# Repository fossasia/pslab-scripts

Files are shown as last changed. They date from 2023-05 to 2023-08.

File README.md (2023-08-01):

# PSLab

This repo is used for scripts and operators that collect data of specific sensors connected with the PSLab.




PSLab is a tiny pocket science lab that provides an array of equipment for doing science and engineering experiments. It can function like an oscilloscope, waveform generator, frequency counter, programmable voltage and current source and also as a data logger. Our website is at https://pslab.io

## The PSLab Sensor Box

For a quick start jump to the [initial setup](#initial-setup) or the [basic usage](#basic-usage) section.

<p align="center">
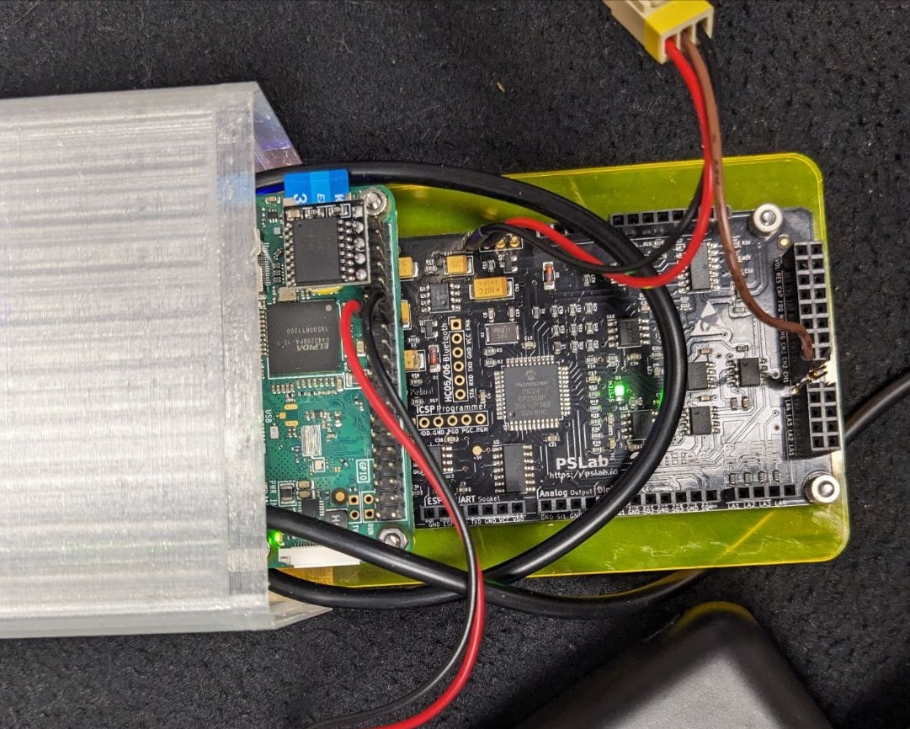
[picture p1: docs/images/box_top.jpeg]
PSLab Sensor Box
    
</p>

In this project four different experimental setups of the [PSLab v5](https://pslab.io/wp-content/uploads/PSLab-Data-Sheet.pdf) are created, each incorporating a different sensor: one measuring [CO2](/docs/sensors.md#⬛-co2e-sensor-ccs811), one for [oxygen](/docs/sensors.md#🟦-oxygen-sensor-ao-03), one for [temperature](/docs/sensors.md#🟩-temperature-sensor-lm35), as well as one setup measuring the [light intensity in lux](/docs/sensors.md#🟨-light-intensity-sensor-gl5528).
Details for those sensor setups can be found in the [docs](/docs/sensors.md).

In addition, the following **hardware components** are connected to the PSLabs:

- A **Raspberry Pi Zero W** to store the sensor data permanently on an SD card and, at the same time, make this data available via the Raspberry Pi's WiFi module. The "Zero" is especially handy here, as it is the most lightweight Raspberry Pi version. Both, the Raspi and the PSLab are screwed on to a plexiglass panel that is slid into the box using the boxe's integrated rail system.
- A **Button** to safely shutdown the Raspberry Pi. It needs to be long pressed for at least one second in order to trigger the device's shutdown. Here, one button terminal is plugged into GPIO pin 27, while the other terminal is plugged to the ground.
- The high accuracy I²C **real time clock (RTC)** model [DS3231](https://www.analog.com/media/en/technical-documentation/data-sheets/DS3231.pdf). It contains a small battery and ensures that the device's time progresses, even if the main power source is unavailable. This RTC therefore makes timestamps in the output data possible during times, where the PSLab sensor box can not access the internet. The five pins of this Pi HAT are plugged into pins 1, 3, 5, 7 and 9 of the Raspberry Pi Zero W.
- A 3D printed, splashproof [casing](/docs/casing/README.md) with a USB c port and a lasercut shield to hold the electronics securely in place.

The following **features** are implemented on top of that:

- Each measured data point is then immediately shared via OSC as `/<item_name> <measured_value>, <unit>, <timestamp>`. Additionally it is written into the CSV file of this measurement session. The file is structured as `<timestamp>, <measured_value>, <unit>, <item_name>`.
- The devices are connected to a public WiFi Network, where they share their data as part of an IoT approach. Initially, each device opened their own WiFi Hotspot, however this was later **discontinued**, as the new requirement of accessing all devices within one common network came up.
- A [samba file sharing server](https://raspberrypi-guide.github.io/filesharing/filesharing-raspberry-pi) makes the folder "/home/foss/data" of the Raspberry Pi publicly available to all devices within the WiFi Hotspot. This also enables users to modify or delete the CSV measurement data within this folder remotely via their PC or mobile phone. The measurements are not only provided to this file sharing server in real-time, but also stored on the SD card permanently.
- The measurement it triggered automatically after startup. This is done by a custom [systemd](https://www.raspberrypi-spy.co.uk/2015/10/how-to-autorun-a-python-script-on-boot-using-systemd/) service.
- The Raspberry Pi itself is running the code from the master branch this Github repository. This makes code updates easy to distribute on all devices. All PSLab sensor boxes run the exact identical code, with the only difference being the experiment type parameter with which `init_pipe.py` is called by the systemd service.

## Accessing the Raspberry Pi

In order to modify the software, the data on the Raspberry Pi's SD card needs to be accessed.
This can either be done by plugging the SD card into a computer, accessing the Raspberry Pi via SSH, or by using the Raspi as a computer itself. In the following, the latter two methods are explained in detail.
In any case, the SD card should never be cleared fully, because this would delete the operating system and therefore stop the Raspberry Pi from working.

### Using the Raspberry Pi as an Independent Computer

Here, a monitor needs to be connected to the microHDMI slot of the Raspi. Simultaneously a mouse and a keyboard need to be linked to the inner microUSB slot via an USB hub. Make sure to perform this cabling-up before attaching the device to the electricity source.

### Accessing the Raspberry Pi via SSH

An [SSH access](https://itsfoss.com/ssh-into-raspberry/) can be more convenient, as there is no additional cabling needed.
However, to establish this connection, the Raspberry Pi needs to be in the same WiFi network as the connecting laptop. If that is not the case yet, there is no way around connecting the Raspi to a monitor first, in oder to set up this WiFi connection, as the Raspberry Pi Zero W does not have a LAN port. Also, the network specific **IP address** of the Raspberry Pi needs to be known. It can be retrieved by executing the command `ifconfig` in the Raspi's terminal while having it connected to a monitor. The IP address can then usually be found in the "wlan0" paragraph and is formatted in a "000.000.000.000" pattern.
To then establish the ssh connection, the following steps need to be executed:

1. Ensure that the PC is connected to the same WiFi Hotspot as the PSLab Sensor Box.
2. Open the SSH connection by running `ssh foss@<ip>` in the PC's terminal and entering the password `foss` when asked.
3. Now you are operating on the Raspberry Pi.

## Initial Setup

Before using the devices in an own network, a one time setup is needed.
Once this is done, for every following usage, please directly jump to the [basic usage](#basic-usage) section.

Both, the OSC messages and the CSV file, of the measurement can be retrieved via WiFi.
Currently, the devices are connected to a dummy WiFi Hotspot with the credentials `myHotspot` as the SSID and `password123` as the password.
Thus, for basic testing, one can just open a Hotspot with these details on a Phone/PC, the devices will automatically connect and the measurement data can be obtained.

However, for more extensive usage, it is obviously more convenient to connect the PSLab Sensor Boxes to the buildings usual WiFi.
For example a connection to eduroam can be established by [logging in with one's university credentials](https://www.uni-weimar.de/fileadmin/user/uni/zentrale_einrichtungen/scc/wlan/Ubuntu.pdf).
The network connection can be changed by [connecting the Raspberry Pi to a monitor](#using-the-raspberry-pi-as-an-independent-computer) and logging into the new WiFi Hotspot using the graphical user interface. Once connected, it is also possible to [set a static private IP address](https://www.tomshardware.com/how-to/static-ip-raspberry-pi) for the Raspberry Pi in this network.
This can be very useful, for example, in order to make the Raspi reliably accessible via SSH.
Please make sure that the devices can see each other in the network and disable/ reconfigure the [VLAN](https://www.techtarget.com/searchnetworking/definition/virtual-LAN), in case one is set up.

Additionally, the IP address and port of the OSC server, need to be edited according to the actual address of the OSC receiver.
This can be done by adjusting the `OSC_RECEIVER_IP` and the `OSC_RECEIVER_PORT` constants on the Raspberry Pis.
The only loophole to this, is to use a OSC server at the pre-configured IP address of `192.168.173.152`.
However, that's not always possible, depending on the available namespace of the network.

## Basic Usage

Once a power source (power bank or cord to electricity outlet) is connected to the PSLab sensor box and the device has fully booted (this **may take a minute ot two**), a new measurement is automatically started. The measurement results are now simultaneously shared via the [Open Sound Control Protocol (OSC)](https://en.wikipedia.org/wiki/Open_Sound_Control) and collected in a [CSV](https://en.wikipedia.org/wiki/Comma-separated_values) file.
To retrieve this data, please connect your own PC/Phone to the same public WiFi Hotspot, that the PSLab Sensor Box is connected to (see [initial setup](#initial-setup)).

### Accessing the CSV Measurements

The CSV measurements of each PSLab sensor box can be retrieved in real time from the file server via WiFi:

1. A detailed manual on how to connect to the devices file server for the first time can be found in the [docs](/docs/network_connection_manual.md).
2. Once connected, the PSLab will appear in the "Network Devices" section.
<p align="center">
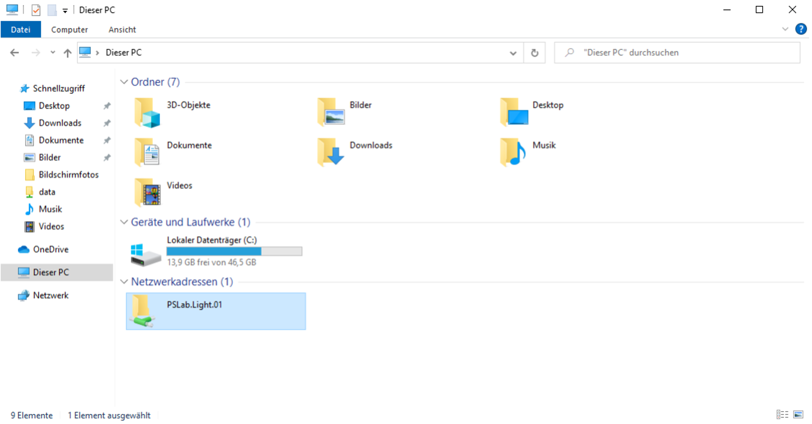
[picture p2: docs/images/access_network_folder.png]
Access network device
    
</p>
Access the data folder and fetch the most recent CSV measurement data file. This file can for example be opened by Excel or just a normal text editor. The current measurement file is updated automatically every few seconds, to see these real time changes, just close and reopen the file.

<p align="center">
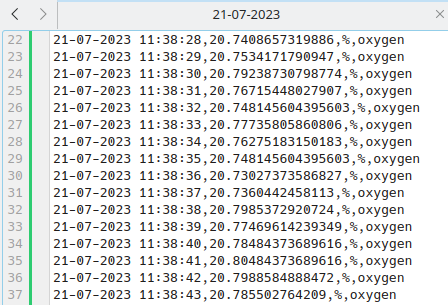
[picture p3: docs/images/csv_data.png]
Sample CSV
    
</p>

Analysis tasks can now be performed on these data sheets, for example by importing them into [Jupyter Notebook](https://jupyter.org/).

### Receiving the OSC Messages

The OSC messages are sent to the specified IP address upon startup. To receive those messages a OSC server like this is necessary:

```[python]
import argparse
from pythonosc.dispatcher import Dispatcher
from pythonosc import osc_server

if __name__ == "__main__":
    parser = argparse.ArgumentParser()
    parser.add_argument("--ip", default="192.168.173.152")
    parser.add_argument("--port", type=int, default=5005)
    args = parser.parse_args()

    dispatcher = Dispatcher()
    dispatcher.map("/light", print)
    dispatcher.map("/temp", print)
    dispatcher.map("/co2", print)
    dispatcher.map("/oxygen", print)

    server = osc_server.ThreadingOSCUDPServer(
        (args.ip, args.port), dispatcher)
    server.serve_forever()
```

This server uses the [python-osc](https://github.com/attwad/python-osc) package to receive and decode the messages. The package can be installed by executing `pip3 install python-osc` in the PC's terminal.
Please note that this setup only works if the IP address, specified as `OSC_RECEIVER_IP`, is identical to the IP address stated in the server scrips (in line 7 here) and corresponds to the laptops own IP address (obtainable by executing "ifconfig" in the terminal). This OSC server for example produces the following output when, at the same time, the Oxygen Sensor Box and the Light Sensor Box are sending OSC data to this IP address at port 5005:

<p align="center">
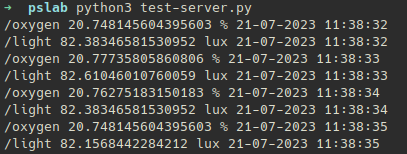
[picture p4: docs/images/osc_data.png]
Sample OSC
    
</p>

### Example Measurement Session

When for example using the PSLab Sensor Box "Lux", changes in the environment's light intensity can be measured.
After attaching the box to a power bank and waiting for two minutes, the device starts measuring.

<p align="center">
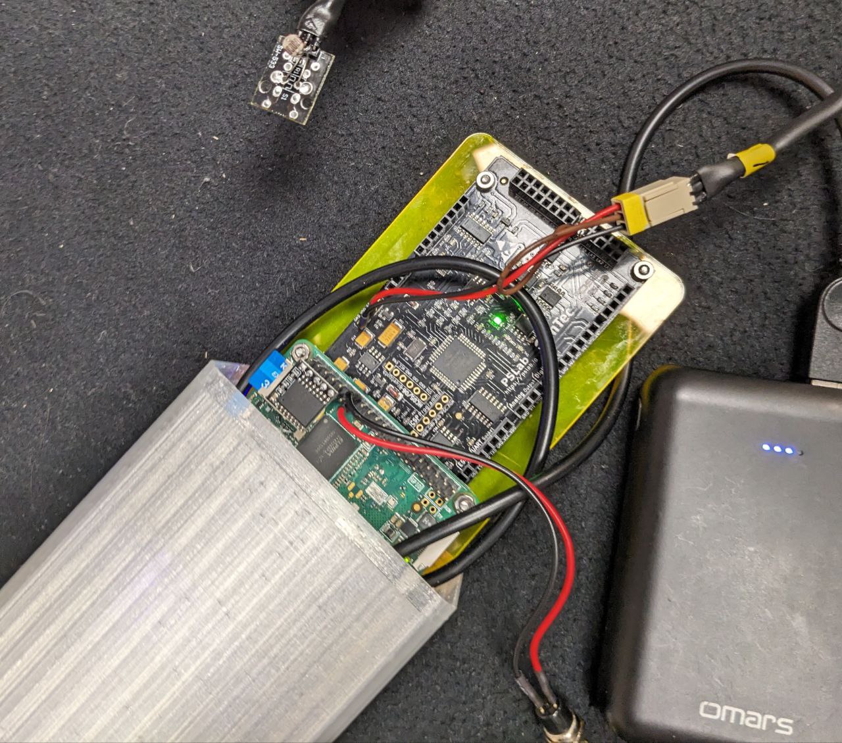
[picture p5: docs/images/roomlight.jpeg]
Lux sensor at room light
    
</p>

The running OSC server on our laptop, that is connected to the same WiFi Hotspot as the Sensor Box, then receives the following data:

```
/light 109.5234702837157 lux 21-07-2023 20:44:12
/light 108.62976013160224 lux 21-07-2023 20:44:13
/light 114.54458695414951 lux 21-07-2023 20:44:14
```

To test the sensor and observe the changes in the environment, the lights are now turned off.

<p align="center">
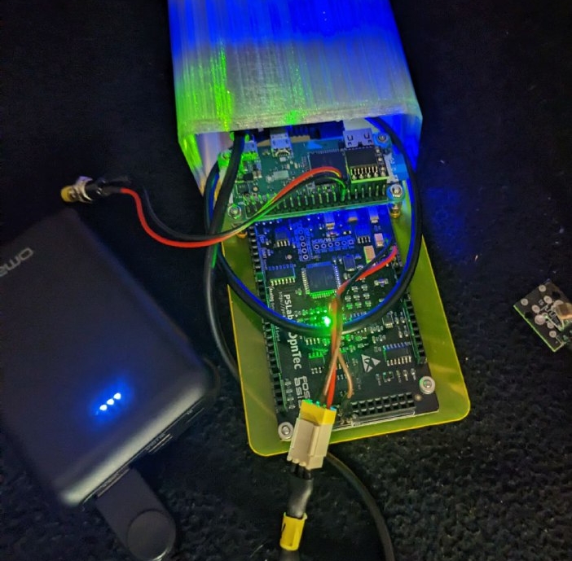
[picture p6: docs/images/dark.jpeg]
Lux sensor at darkness
    
</p>

This results in the following OSC messages:

```
/light 6.80740388396548 lux 21-07-2023 20:46:04
/light 7.05431189748499 lux 21-07-2023 20:46:05
/light 7.52577384043171 lux 21-07-2023 20:46:06
```

To then test the sensor at a very hight brightness, we turned the lights on again and exposed the photoresistor to a flashlight:

<p align="center">
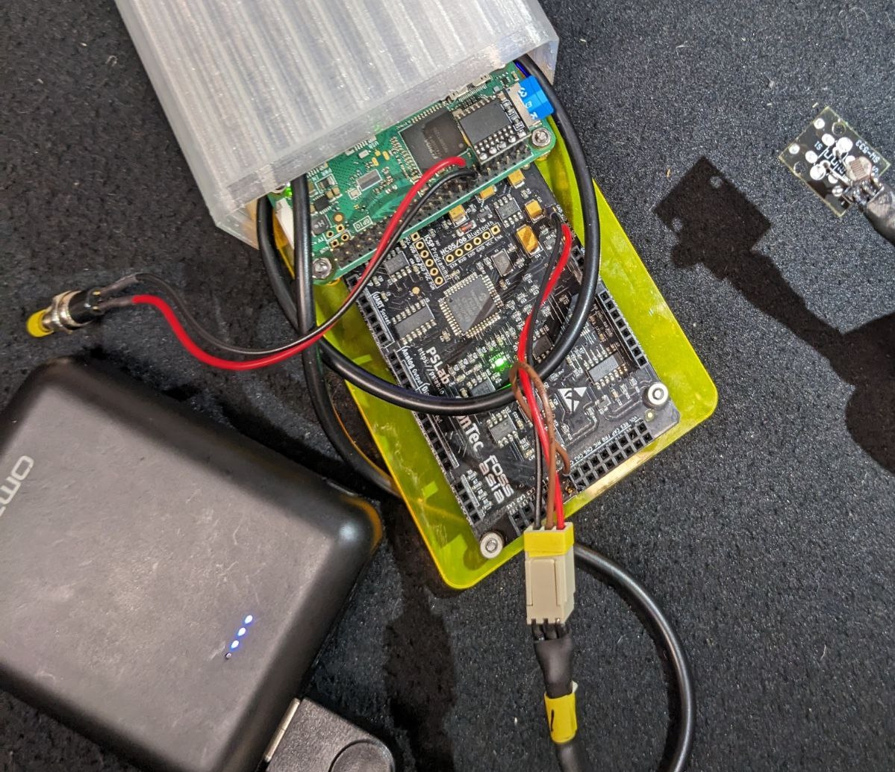
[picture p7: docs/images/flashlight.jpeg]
Lux sensor at flashlight
    
</p>

Thus, the OSC server receives these messages:

```
/light 1721.79974583536023 lux 21-07-2023 20:47:38
/light 1902.29013779831879 lux 21-07-2023 20:47:39
/light 1483.70672770591856 lux 21-07-2023 20:46:40
```

In an analogue way, the temperature sensor can be tested by warming it up with one's finger tips,
while the CO2 and oxygen sensors can by tested by exposing them to exhaled air.

### Ending the Session

To eventually trigger the shut down process of the Raspberry Pi, please press the attached button for one to two seconds.
After waiting 20-30 seconds, the shut down is completed, the green indication light on the Raspberry Pi goes off and the electricity source can be unplugged.
Technically, the measurement session can also be terminated by just unplugging the power source directly, however in the long term,
this technique can be harmful for the Raspberry Pi's file system.

## Debugging

As this is a hardware project, it is not unlikely that at some point in time, one of the cables or other components will cause problems. To then solve this, it is important to localize the error. Here, different levels of debugging can help, depending on the supposed location of the problem.
Basic debugging steps may be:

- Turn the Raspberry Pi off (by using the button) and on again (by plugging in a power bank).
- Make sure all cables are attached firmly. Try unplugging and reattaching them.
- Sometimes the output voltage of a laptop's USB port might vary a bit to much, try using a power bank instead.
- Make sure the lights on the PSLab are glowing. Otherwise there probably is a problem with the boxes' charging cable or the PSLab itself.
- Make sure the light on the Raspberry Pi is glowing or blinking. This indicates a successful booting of the Raspbian OS.
- Try using one PSLab Sensor Box after another, not in parallel.
- If the device does not connect to the WiFi network (for example checkable via Linux' `nmap` tool), try having the network open already during the Raspberry Pi's booting process.
- Try opening the Hotspot, that the Sensor Boxes are connected to, from another device (e.g. phone, instead of laptop).

Some more advanced debugging techniques include the following:

### Debugging Sensor Issues - On a PC

To ensure that the PSLab itself and the sensor are working properly,  the following test can be executed.
Please note that this routine is the only one that is executed on a normal (Linux)
**PC, instead of the Raspberry Pi**, in order to abstract from any Raspi specific problems.

1. Ensure that python3 is installed on your PC by running `python3 --version` in the terminal. In case there is no item found, install version 3.6 by `sudo apt-get install python3.6` and reboot your system afterwards to ensure that everything is fully loaded.
2. Install the pslab-python library on the PC by executing `pip3 install pslab`.
3. Detach the PSLab and the corresponding sensor from the Raspberry Pi by removing the
microUSB to microUSB cable between Raspi and PSLab. Instead connect the microUSB port of the PSLab to one of the PC's USB ports.
4. Download the pslab-scripts library by running `sudo git clone https://github.com/fossasia/pslab-scripts.git`.
5. Open the repository folder by executing `cd pslab-scrips`.
6. Start the execution a sensor type specific test by running `sudo python3 init_pipe.py <type>` (for example
`sudo python3 init_pipe.py oxygen`). This execution can always be stopped by hitting ctrl+c.
7. Check the fetched measurement data by accessing the file located in `/home/<user name>/data`.

### Debugging the Startup Script - On the Raspberry Pi

Often times the script itself actually works fine, but the startup manager might start it
too early, causing resource conflicts and other issues to arise.
One option to debug this, is to first make sure that the script itself works fine by running `sudo python3 /home/foss/code/init_pipe.py <type>`
on the Raspberry Pi (for example `sudo python3 init_pipe.py oxygen`) and checking the results in
`/home/foss/data`. If those results look good, but the data fetching upon startup still does not work, the error logs of the startup script can be examined by executing `journalctl -u startup.service --since yesterday` in the Raspi's terminal.

## Advanced Usage

Different software and hardware projects can be realized on this combination of PSLab and Raspberry Pi.
Some ideas for modifying the existing software are listed below.
As python3, the pslab-python library, as well as this pslab-scripts repository, are already installed on the Raspberry Pis, **no** additional installation is needed here.

### Adjusting the measurement interval

Currently a new data point is retrieved from the sensor every second. This can be changed by adjusting the value for the`MEASURING_INTERVAL`. This constant can be found in the `/home/foss/pslab-scripts/measure.py` file on the Raspberry Pi.

### Adjusting the flushing interval

The data points are flushed into the CSV file after every 10 measurements in the current implementation. To change this, the `FLUSHING_THRESHOLD` value in `/home/foss/pslab-scripts/store_data.py` can be adjusted on the Raspi.

### Accessing the continuous measurement data stream via an API

As of now, the measurement data is redirected into a CSV file and OSC messages by the pipe function. This can however be modified freely, for example by adding an additional step 
to transform and output some data into the data exporting function.
This new process can freely process the measured data points, received via `connection.recv()`.

### Fetching a software update from Github

1. Open the terminal.
2. Open the folder "pslab-scripts" by typing `cd /home/foss/pslab-scripts`.
3. Enter `git pull` in the terminal to fetch the new changes in software.

### Changing the sensor type

By adjusting the experiment type parameter in the systemd service "startup.service", the supported sensor type of this specific PSLab sensor box can be changed easily:

1. Open a terminal.
2. Type `sudo nano /lib/systemd/system/startup.service`.
3. The "startup.service" file is now opened in a simple text editor. Here, you can adjust the experiment type parameter, e.g. from "light" to "co2", in case the PSLab sensor box for light shall now be used with a CO2 sensor. Besides "light" and "co2", also "oxygen" and "temp", are supported as parameters here.
4. Save the changes by pressing ctrl+o. Exit the editor by pressing ctrl+x.
5. The changes take effect once the device is rebooted. This can for example be done by executing `sudo reboot`.

## Repository Structure

```
📦pslab-scripts
 ┣ 📂docs                               # Supplementary material
 ┃ ┣ 📂ao-03_amplifier_circuit_design  # KiCad project files of the custom circuit board for the AO-03 sensor
 ┃ ┃ ┗ 📜...
 ┃ ┣ 📂casing                          # Information about the 3d printed casing, as well as the lasercut shield
 ┃ ┃ ┣ 📜README.md
 ┃ ┃ ┗ 📜...
 ┃ ┣ 📂images
 ┃ ┃ ┗ 📜...
 ┃ ┣ 📂logos                           # Sticker designs for the boxes (made with Inkscape)
 ┃ ┃ ┗ 📜...
 ┃ ┣ 📜network_connection_manual.md    # Manual on how to connect a device to the PSLab's file server
 ┃ ┣ 📜presentation_may28.pdf
 ┃ ┣ 📜sensors.md                      # Detailed descriptions of all four sensor setups
 ┃ ┗ 📜testing_manual.md               # Detailed manual on how to test the devices
 ┣ 📂sensors                            # Contains a specific run script for every sensor
 ┃ ┣ 📜ao03_oxygen.py
 ┃ ┣ 📜ccs811_co2.py
 ┃ ┣ 📜driver_ccs811.py                # Custom driver for the CCS811 sensor
 ┃ ┣ 📜gl5528_light.py
 ┃ ┗ 📜lm35_temp.py
 ┣ 📜export_data.py                     # Sharing the measurements via OSC and CSV
 ┣ 📜init_pipe.py                       # Main project file
 ┣ 📜measure.py
 ┗ 📜shutdown.py                        # Script for the button logic
```

## Buy

* You can get a Pocket Science Lab device from the [FOSSASIA Shop](https://fossasia.com).
* More resellers are listed on the [PSLab website](https://pslab.io/shop/).

## Communication

* The PSLab [chat channel is on Gitter](https://gitter.im/fossasia/pslab).
* Please also join us on the [PSLab Mailing List](https://groups.google.com/forum/#!forum/pslab-fossasia).

## Site

The website is hosted on [pslab.io](http://pslab.io).

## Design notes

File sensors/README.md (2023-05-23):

Currently the following sensors are supported by specific firmware here, however [others](https://pslab.io/sensors/) could be added later on.

## CO<sub>2</sub>e Sensor: [CCS811](https://cdn.sparkfun.com/assets/learn_tutorials/1/4/3/CCS811_Datasheet-DS000459.pdf)

This digital sensor is embedded on the [CJMCU-8118](https://www.amazon.co.jp/-/en/CJMCU-8118-HDC1080-Monoxide-Temperature-Humidity/dp/B07KWPHYLY) circuit board and powered by a custom [driver](https://github.com/fossasia/pslab-python/tree/development/pslab/external) that uses the sensors I²C protocol.

The CCS811 measures the [CO<sub>2</sub>e](https://klima.com/blog/what-is-co2e/) ("CO<sub>2</sub> equivalent") value of the surrounding air in particles per million (ppm). This value also incorporates the levels of methane (CH<sub>4</sub>), nitrous dioxide (N<sub>2</sub>O) and other synthetic gases, besides the regular CO<sub>2</sub> measurement, which makes up about 75% of the CO<sub>2</sub>e. This value is therefore used by environmental scientists nowadays to give more accurate measurements about the current levels of emissions in the air.

As emissions vary depending on the air's temperature and humidity, the CCS811 sensor has inbuilt temperature and moisture sensors. It uses those to offset the variation of the measuring conditions to the optimal lab conditions. However, it is important to notice that the sensor has a lower limit of 400ppm CO<sub>2</sub>e that can be detected.

## Oxygen Sensor: [AO-03](http://www.aosong.com/userfiles/files/media/Datasheet%20AO-03.pdf)

The analog AO-03 sensor measures the O<sub>2</sub> content of the surrounding air in percent (%). It is embedded in a custom circuit board that is amplifying the measured voltage, because the changes in oxygen levels are usually just very slight and therefore the changes in voltage are also only minimal.

<p align="center">
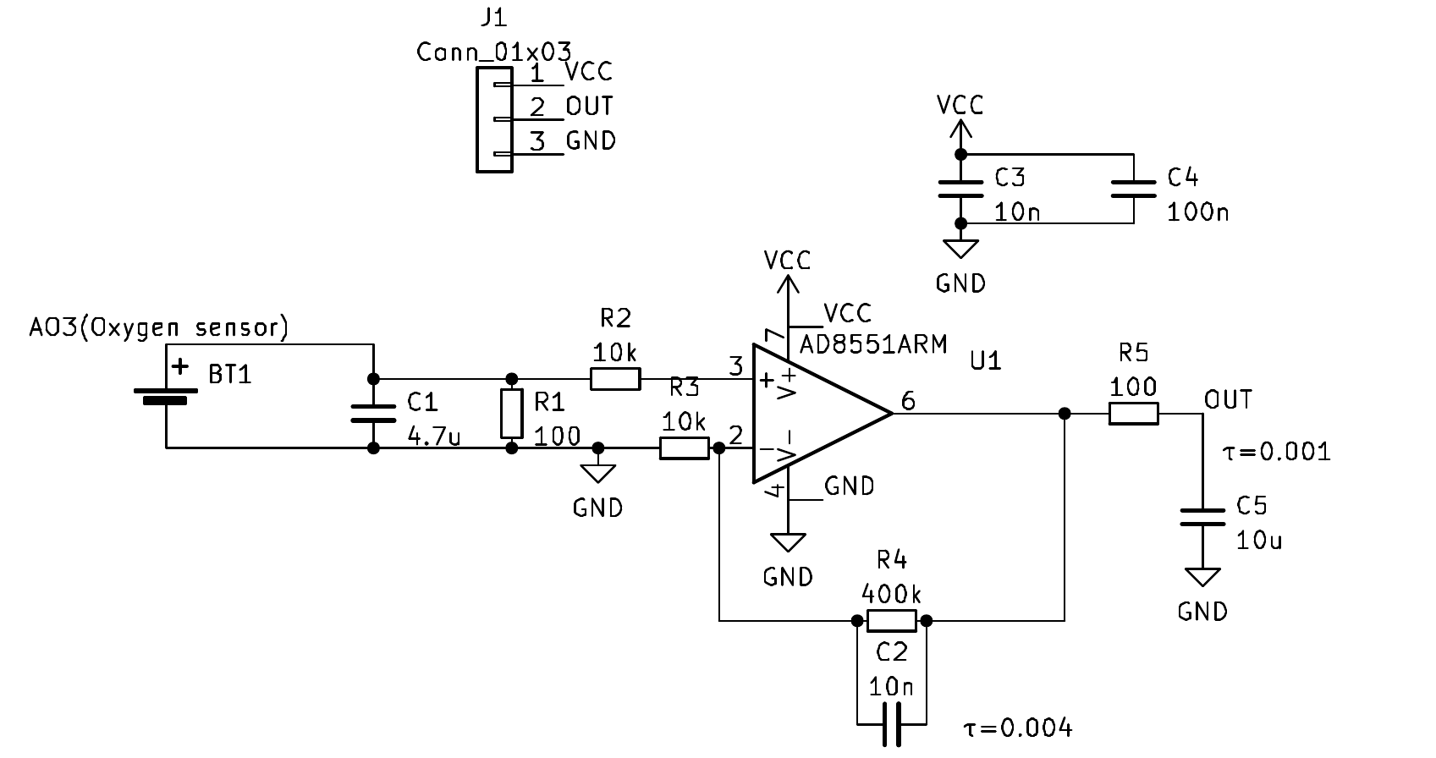
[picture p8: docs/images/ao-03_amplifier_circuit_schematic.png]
Schematic of the amplifier board
    
    <p>[Custom designed](../docs/ao-03_amplifier_circuit_design/) amplifying circuit board for the AO-03 oxygen sensor.</p>
</p>

## Light Intensity Sensor: [GL5528](https://pi.gate.ac.uk/pages/airpi-files/PD0001.pdf)

A light sensitive photo-resistor is used to measure the luminous intensity of the surrounding light waves in lumen per square meter (lux). The resistance of this sensor is measured within a voltage divider circuit with a second resistor of 10k Ohm. This value can then easily be transformed into the actual light intensity. Be aware that the luminous intensity is rising exponentially fast with increasing brightness levels of the environment.

## Temperature Sensor: [LM35](https://www.ti.com/lit/ds/symlink/lm35.pdf)

This analog thermometer can measure temperatures between −55°C and 150°C. It guarantees an accuracy of +/- 1°C over the whole range.

## Connecting the Sensors
<p align="center">
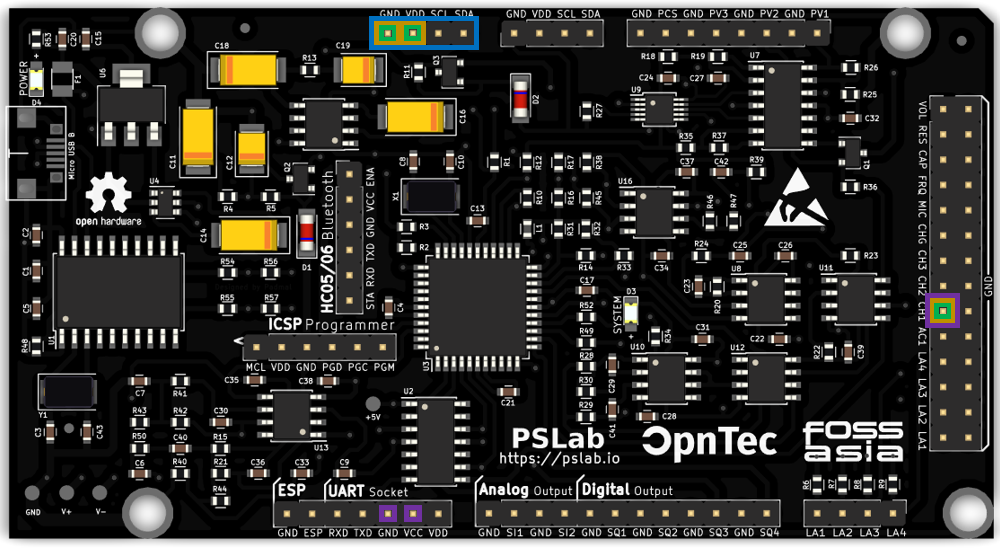
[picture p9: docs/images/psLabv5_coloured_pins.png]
Color coded sensor connections
    
</p>

- **CO<sub>2</sub>e: blue pins.** 'VCC' to the PSLab's VDD (3.3V power supply), 'GND' to the PSLab's GND, 'SLC' to the PSLab's SLC (serial clock needed for the I²C protocol) and 'SDA' to the PSLab's SDA (serial data needed for the I²C protocol).
- **Oxygen: orange pins.** 'GND' to the PSLab's GND, 'OUT' to the PSLab's CH1 (analog input to read voltages in range [-16 V, +16 V]) and 'VCC' to the PSLab's VDD (3.3V power supply).
- **Light Intensity: green pins.** '-' to the PSLab's GND, the middle pin to the PSLab's VDD (3.3V power supply) and 'S' to the PSLab's CH1 (analog input to read voltages in range [-16 V, +16 V]).
- **Temperature: purple pins.** Facing the flat side and having the sensor's pins face down: Left pin to the PSLab's VCC (5V power supply), middle pin to the PSLab's CH1 (analog input to read voltages in range [-16 V, +16 V]) and right pin to the PSLab's GND.

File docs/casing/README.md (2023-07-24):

# Casing

As part of open source approach, we want to provide a casing for the PSLab Sensor
Boxes that is individually re-creatable and editable at home.
We therefore decided to design 3d printed boxes with a removable side lid.
To securely keep the PSLab and the Raspberry Pi in place, we furthermore designed a
lasercut acrylic shield to attach the technology onto.
This shield can then be slid tightly into the rail system of the box.
As acrylic often slightly varies in thickness there are two slightly different box options with
differing rail sizes: please measure your acrylic first and then print the suitable box for it.

To make the box splashproof, a special sealing was screwed in place for the output point of the sensor cable.
Also, a USB to USB c in socket was installed to simplify attaching the device to a power source.

<p align="center">
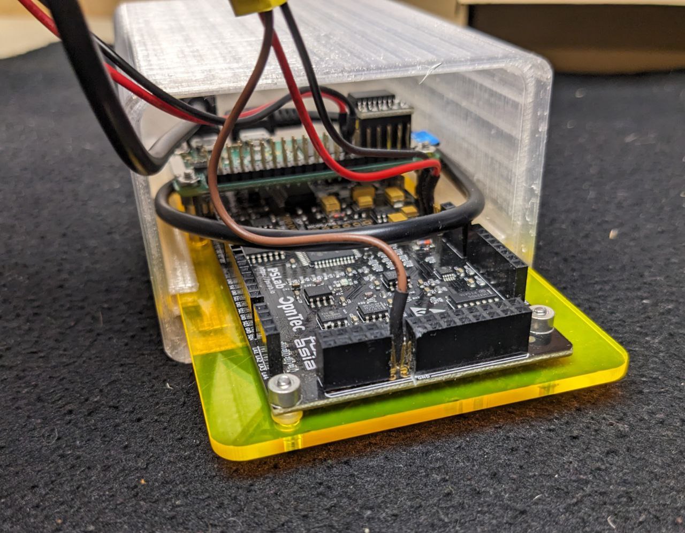
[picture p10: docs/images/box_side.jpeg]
Casing
    
</p>

## Required Materials

- An 8x14cm piece of 3mm thick acrylic
- About 100g of (PLA) filament for the boxes' body
- About 25g of (PLA) filament for the boxes' lid
- 4 x M2.5 x 10mm screws to attach the PSLab to the shield
- 4 x M2.5 washers to space the PSLab from the shield
- 4 x M2.5 x 20mm Screws to attach the Raspberry Pi to the shield
- 8 x M2.5 x 5mm or 4 x M2.5 x 10mm spacers to position the Raspberry Pi above the PSLab
- 4 x M2.5 nuts to secure the Raspberry Pi
- Optional: USB to USC c in socket, screwable sealing to output the sensor cable

## Folder Structure

```
📂casing
┣ 📂box_rail_3.5mm               # CAD model of the box made for acrylic shields of a thickness between 3.0 and 3.4 mm.
┃ ┣ 📜prusa_printing_code.gcode # This file can directly be printed on a Prusa i3 MK3S with 0.4 nozzle. Made with Prusa Slicer.
┃ ┗ 📜...
┣ 📂box_rail_3mm                 # CAD model of the box made for acrylic shields of a thickness between 2.5 and 2.9 mm.
┃ ┣ 📜prusa_printing_code.gcode # This file can directly be printed on a Prusa i3 MK3S with 0.6 nozzle. Made with Prusa Slicer.
┃ ┗ 📜...
┣ 📂lid                          # CAD model of the boxes' lid.
┃ ┣ 📜prusa_printing_code.gcode # This file can immediately be printed on a Prusa i3 MK3S with 0.4 nozzle. Made with Prusa Slicer.
┃ ┗ 📜...
┣ 📂shield                       # Lasercut model for the acrylic shield. Designed with Inkscape. Compiled with VisiCad for the lasercutter at FabLab, Berlin.
┗  ━ 📜...
```

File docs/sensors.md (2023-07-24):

# Sensor Setups

Currently the following sensors are supported by specific firmware here, however [others](https://pslab.io/sensors/) could be added later on.

## ⬛ CO<sub>2</sub>e Sensor: [CCS811](https://cdn.sparkfun.com/assets/learn_tutorials/1/4/3/CCS811_Datasheet-DS000459.pdf)

This digital sensor is embedded on the [CJMCU-8118](https://www.amazon.co.jp/-/en/CJMCU-8118-HDC1080-Monoxide-Temperature-Humidity/dp/B07KWPHYLY) circuit board and powered by a custom driver that uses the sensors I²C protocol.

The CCS811 measures the [CO<sub>2</sub>e](https://klima.com/blog/what-is-co2e/) ("CO<sub>2</sub> equivalent") value of the surrounding air in particles per million (ppm). This value also incorporates the levels of methane (CH<sub>4</sub>), nitrous dioxide (N<sub>2</sub>O) and other synthetic gases, besides the regular CO<sub>2</sub> measurement, which makes up about 75% of the CO<sub>2</sub>e. This value is therefore used by environmental scientists nowadays to give more accurate measurements about the current levels of emissions in the air.

As emissions vary depending on the air's temperature and humidity, the CCS811 sensor has inbuilt temperature and moisture sensors. It uses those to offset the variation of the measuring conditions to the optimal lab conditions. Please give the sensor a minute after startup to fully calibrate. However, it is important to notice that the sensor has a lower limit of 400ppm CO<sub>2</sub>e that can be detected.

<p align="center">
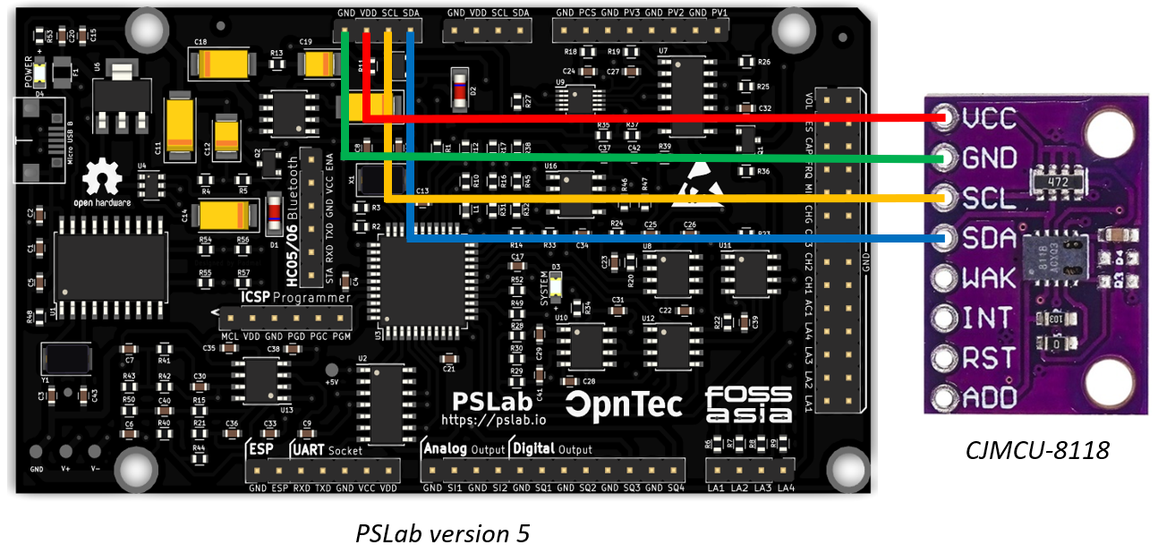
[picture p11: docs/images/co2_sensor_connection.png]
Connecting the co2 sensor
    
</p>
The CJMCU-8118 is connected to the PSLab's VDD (3.3V power supply), GND (ground), SLC (serial clock needed for the I²C protocol) and SDA (serial data needed for the I²C protocol).

## 🟦 Oxygen Sensor: [AO-03](http://www.aosong.com/userfiles/files/media/Datasheet%20AO-03.pdf)

The analog AO-03 sensor measures the O<sub>2</sub> content of the surrounding air in percent (%). It is embedded in a custom circuit board that is amplifying the measured voltage, because the changes in oxygen levels are usually just very slight and therefore the changes in voltage are also only minimal. Please give the sensor a minute after startup to fully calibrate. This AO-03 circuit board is designed as described [below](./ao-03_amplifier_circuit_design/) and depicted in the following:
<p align="center">
    Schematic of the amplifier board
</p>

<p align="center">
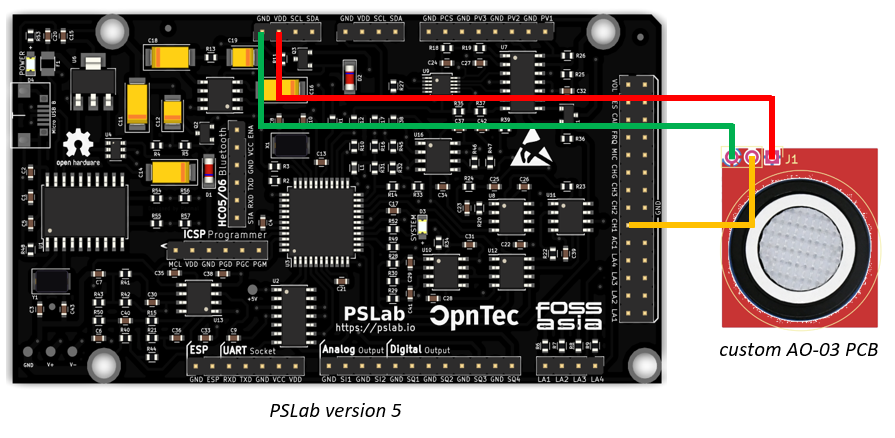
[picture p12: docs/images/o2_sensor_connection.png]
Connecting the o2 sensor
    
</p>
The circuit board is connected to the PSLab's GND (ground), CH1 (analog input to read voltages in range [-16 V, +16 V]) and VDD (3.3V power supply).

## 🟨 Light Intensity Sensor: [GL5528](https://pi.gate.ac.uk/pages/airpi-files/PD0001.pdf)

A light sensitive photo-resistor is used to measure the luminous intensity of the surrounding light waves in lumen per square meter (lux). The resistance of this sensor is measured within a voltage divider circuit with a second resistor of 10k Ohm, inbuilt in the [KY-018 circuit board](https://datasheetspdf.com/pdf-file/1402029/Joy-IT/KY-018/1). This value can then easily be transformed into the actual light intensity. Be aware that the luminous intensity is rising exponentially fast with increasing brightness levels of the environment.

<p align="center">
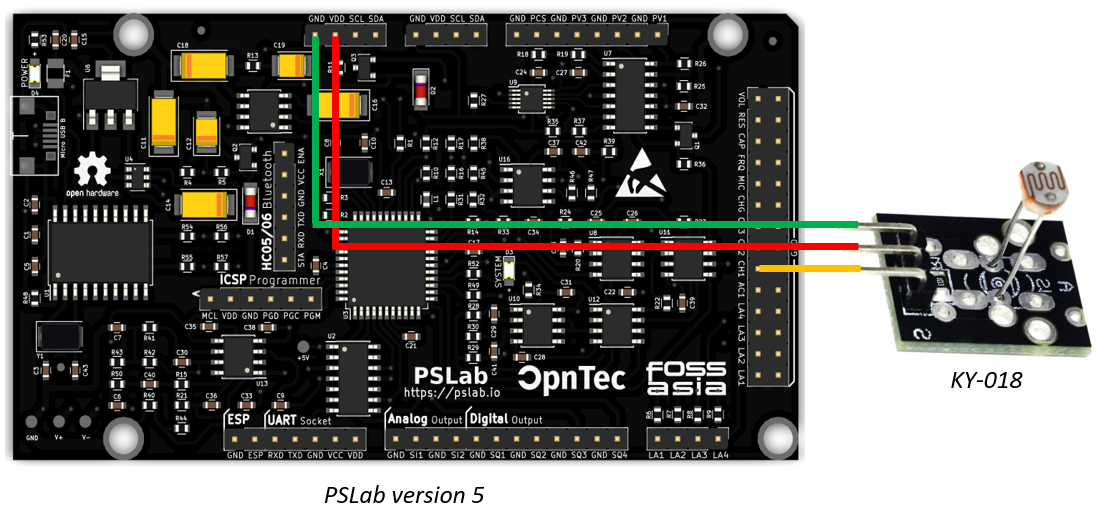
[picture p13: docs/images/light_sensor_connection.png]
Connecting the light sensor
    
</p>
The KY-018 board is connected to the PSLab's GND (ground), VDD (3.3V power supply) and CH1 (analog input to read voltages in range [-16 V, +16 V]).

## 🟩 Temperature Sensor: [LM35](https://www.ti.com/lit/ds/symlink/lm35.pdf)

This analog thermometer can measure temperatures between −55°C and 150°C. It guarantees an accuracy of +/- 1°C over the whole range.

<p align="center">
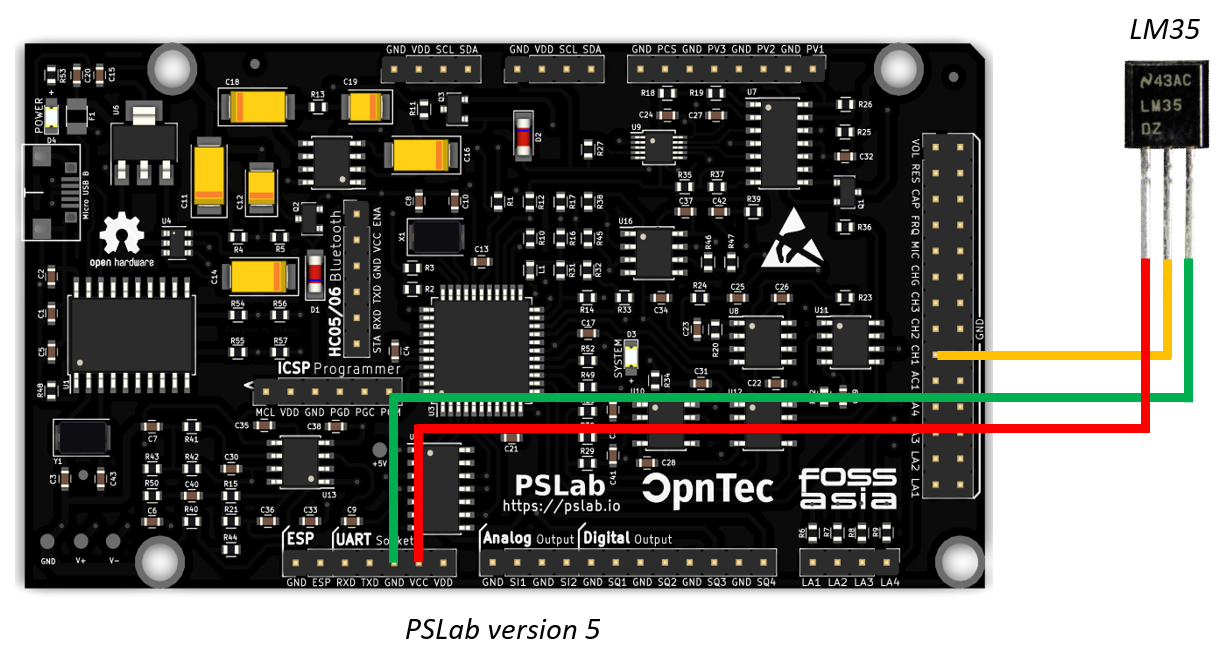
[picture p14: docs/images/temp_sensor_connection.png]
Connecting the temperature sensor
    
</p>
The LM35 is connected to the PSLab's VCC (5V power supply), CH1 (analog input to read voltages in range [-16 V, +16 V]) and GND (ground).

## Sensor Connections

The sensors are linked to the PSLab with reverse polarity protected connectors,
to enable the user to exchange sensors, without the need of unsoldering the jumper cables directly from the PSLab.
In particular, [qwiic connectors](https://www.sparkfun.com/qwiic) were used for the I²C sensors,
as well as regular 3 pin connectors for the analogue sensors.

The connecting cables are color coded as follows:

|                     | Voltage | Ground | Signal |  SDA | SCL    |
|---------------------|---------|--------|--------|----- |--------|
|      **qwiic**      |   red   |  black |        | blue | yellow |
| **3 pin to sensor** |   red   |  brown | yellow |      |        |
|  **3 pin to board** |   red   |  black |  brown |      |        |

Those connectors are then attached to the sensors by about 50cm long cables,
making it for example possible to use the sensor in a climate chamber, while
keeping the box itself outside of it.

In order to make the sensors as water and temperature resistant as possible, their PCBs are covered with conformal coating
and all pin connections are enclosed in, mostly glue coated, shrink tubing.

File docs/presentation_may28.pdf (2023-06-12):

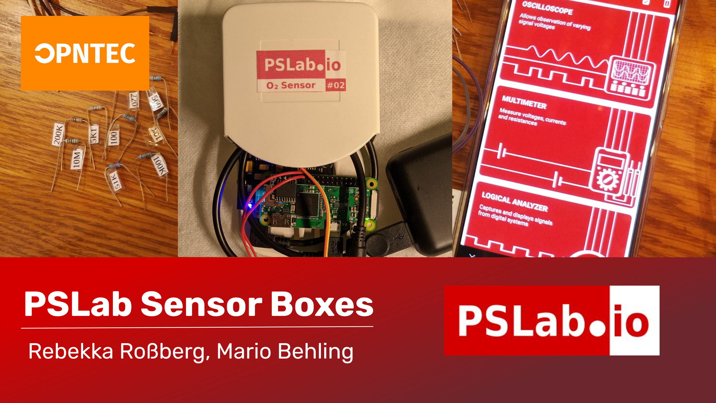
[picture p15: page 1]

# PSLab Sensor Boxes

Rebekka Roßberg, Mario Behling

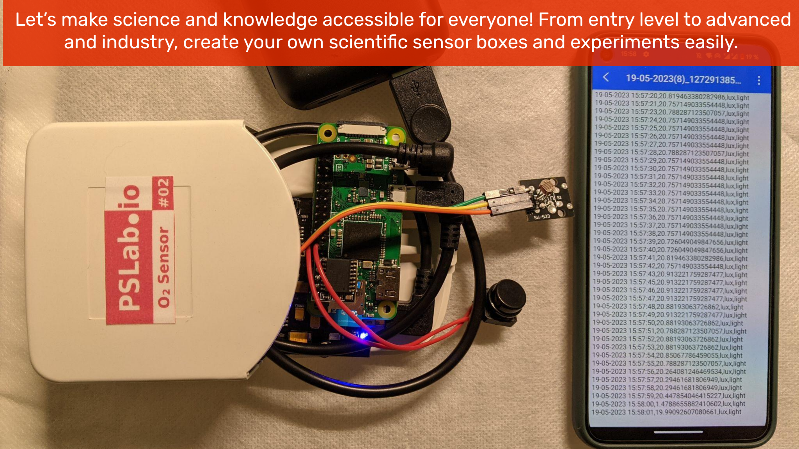
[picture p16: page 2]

Let’s make science and knowledge accessible for everyone! From entry level to advanced and industry, create your own scientific sensor boxes and experiments easily.

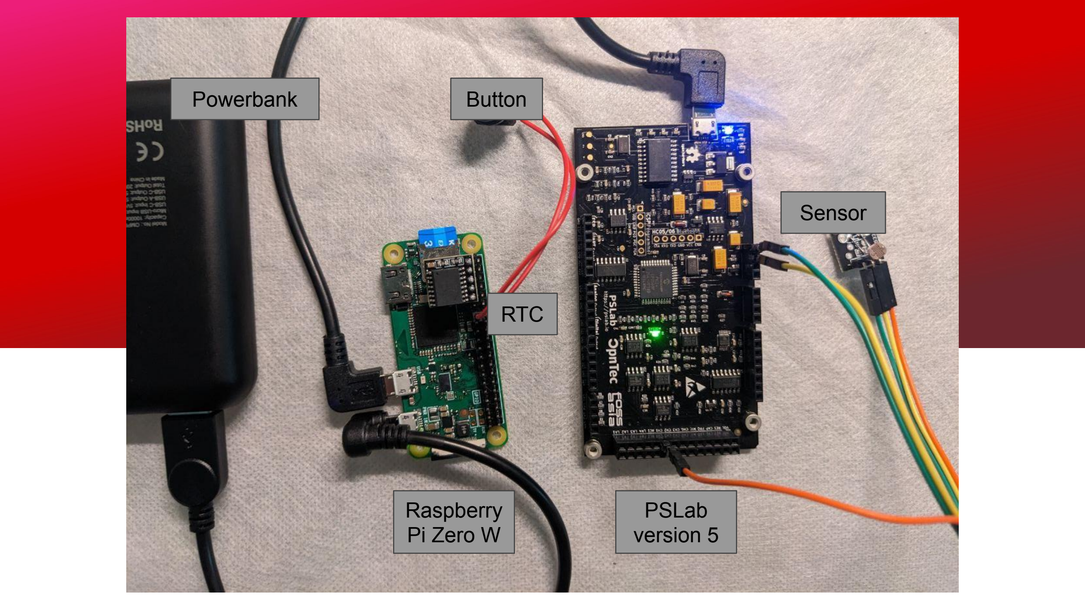
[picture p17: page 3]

Sensor

PSLab
version 5

Button

Raspberry
Pi Zero W

Powerbank

RTC

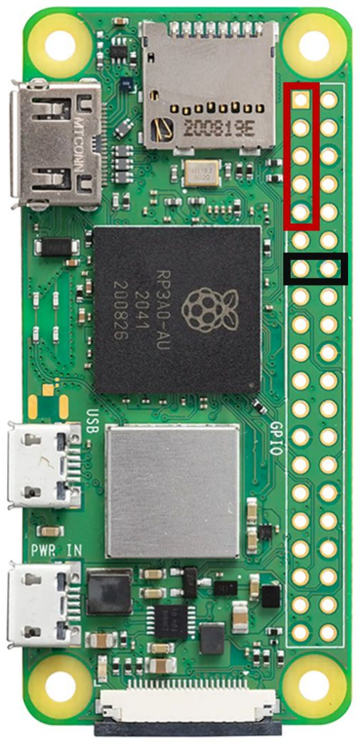
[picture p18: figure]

## Additional Hardware

❖ Raspberry Pi Zero W: for permanent data storage on the SD card and hosting of a file server via the integrated Wi-Fi Hotspot
❖ High Accuracy Real Time Clock: for network independent time stamps in the measurement data ❖ Button: for a safe shutdown
❖ Powerbank: for mobile use

## . Measuring Light Intensity

❖ Measurement in Lux
❖ Using the GL5528 photo-resistor
❖ Embedded within the KY-018’s voltage divider circuit ❖ Value on exponential scale

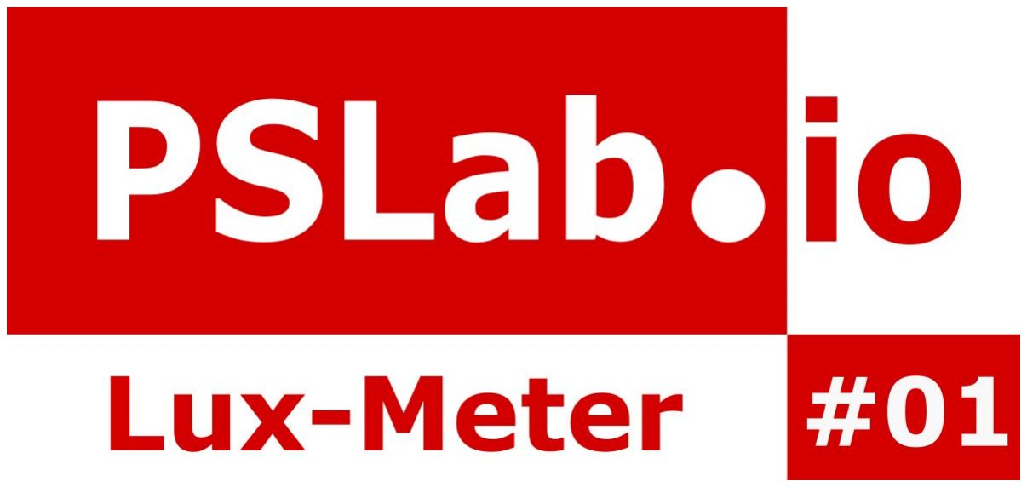
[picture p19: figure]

## Light Intensity Sensor: GL8

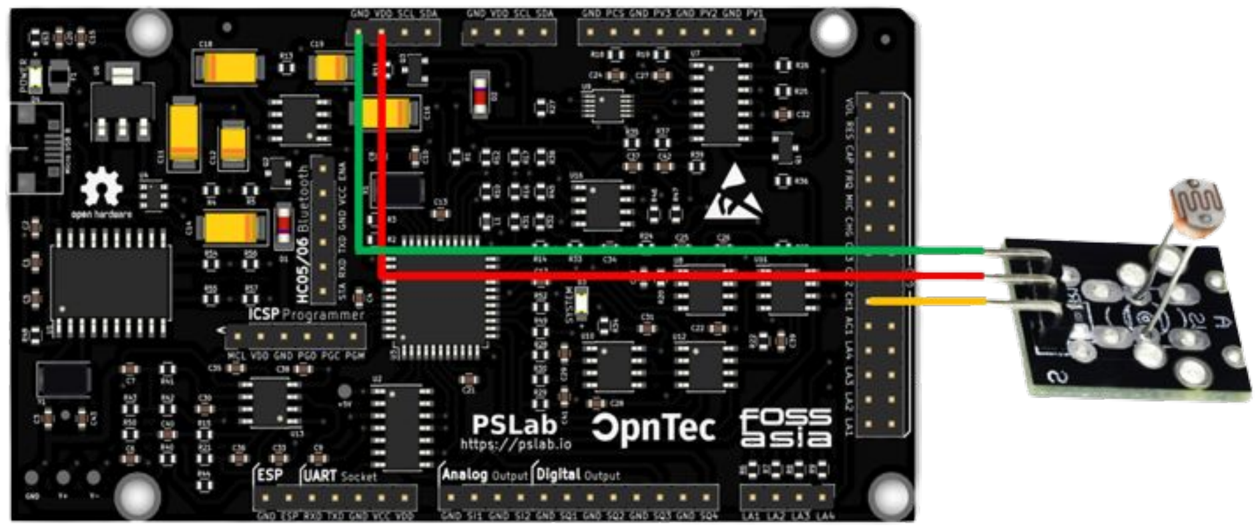
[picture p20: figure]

## . Measuring Temperature

❖ Using the LM35 sensor
❖ Range: - °C to °C
❖ Accuracy: +/- °C

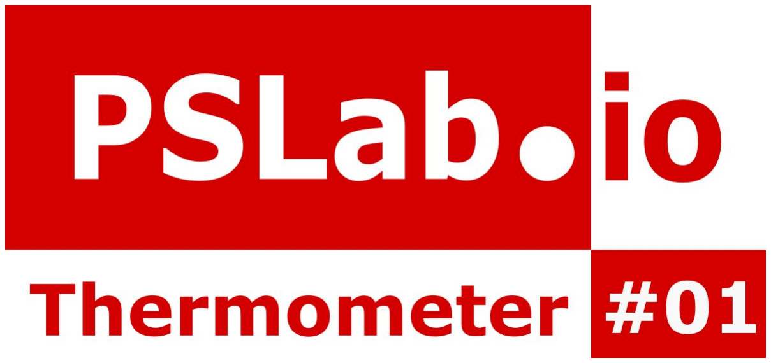
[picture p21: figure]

## Temperature Sensor: LM

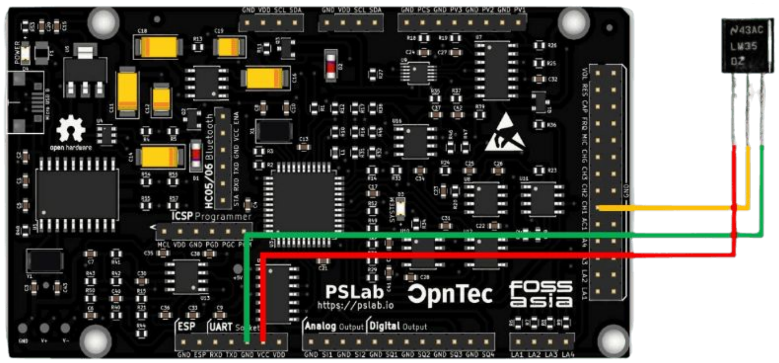
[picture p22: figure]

## . Measuring CO₂

❖ Measurement in particles per million (ppm)
❖ Using the CCS811 sensor for CO₂e quantification:
- Accurate measurement of green house gases ❖ Automatic offset of temperature and humidity
❖ Lower limit of ppm CO₂e
❖ Embedded on the CJMCU-8118
circuit board
❖ With custom I²C driver

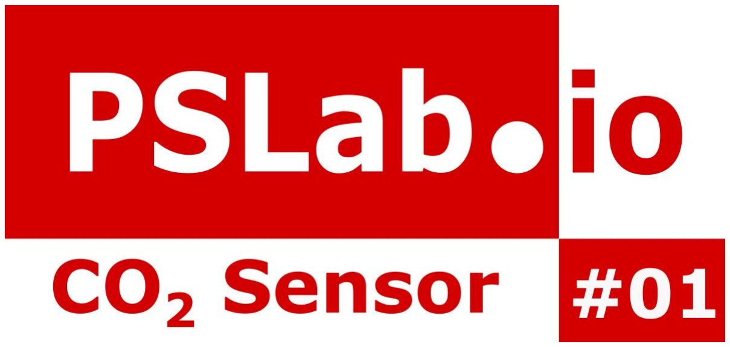
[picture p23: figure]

## CO₂ Sensor: CCS8

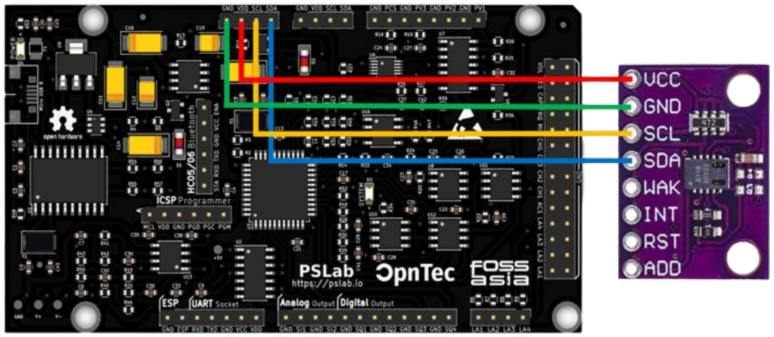
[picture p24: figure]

## . Measuring Oxygen

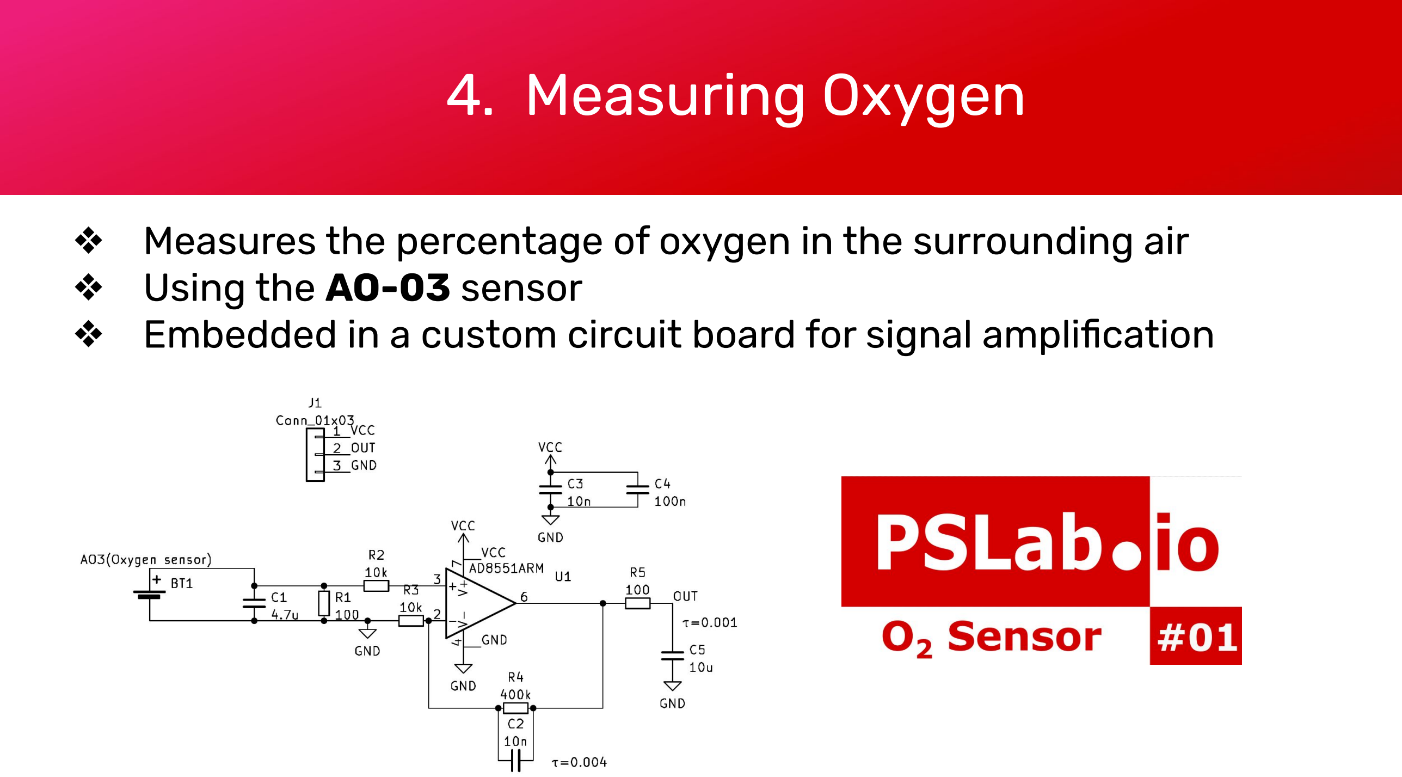
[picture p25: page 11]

❖ Measures the percentage of oxygen in the surrounding air ❖ Using the AO-03 sensor
❖ Embedded in a custom circuit board for signal amplification

## Oxygen Sensor: AO-

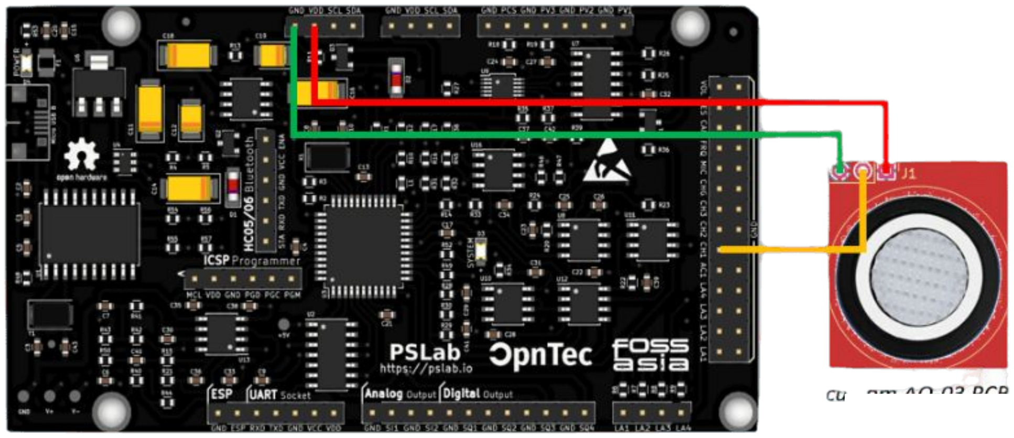
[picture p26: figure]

## Stealth Design for Outdoor Usage

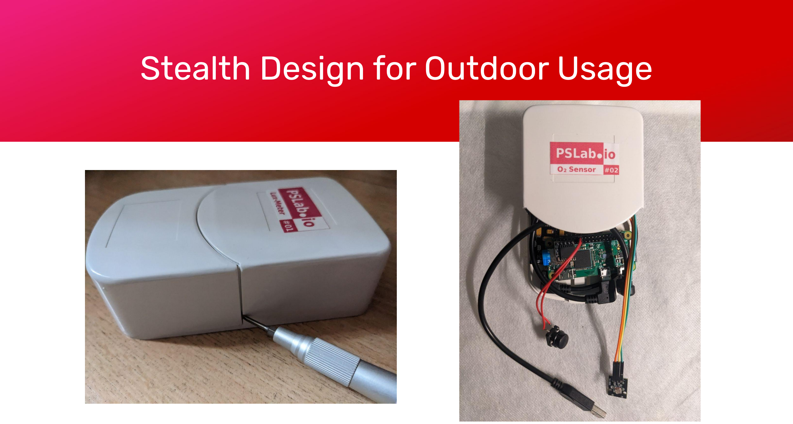
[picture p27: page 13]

## Basic Usage

❖ Plug Power Source into the PSLab Sensor Box
- Measurement starts
- Wi-Fi Hotspot for file sharing is opened
❖ To fetch the measurement data:
- Connect PC/ phone to the corresponding Wi-Fi Hotspot
- Access file server
- Fetch CSV file
❖ Push button to trigger the safe shutdown

## Connecting

❖ Detailed manuals to initialize a connection to the file server can be found in the GitHub Repository (https://github.com/fossasia/pslab-scripts)
❖ Currently Windows, Mac, Linux, Android, and iPhone are supported there

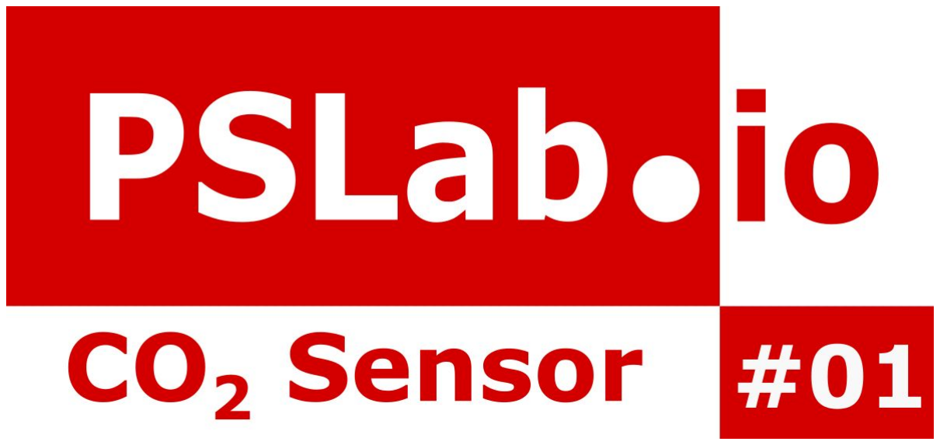
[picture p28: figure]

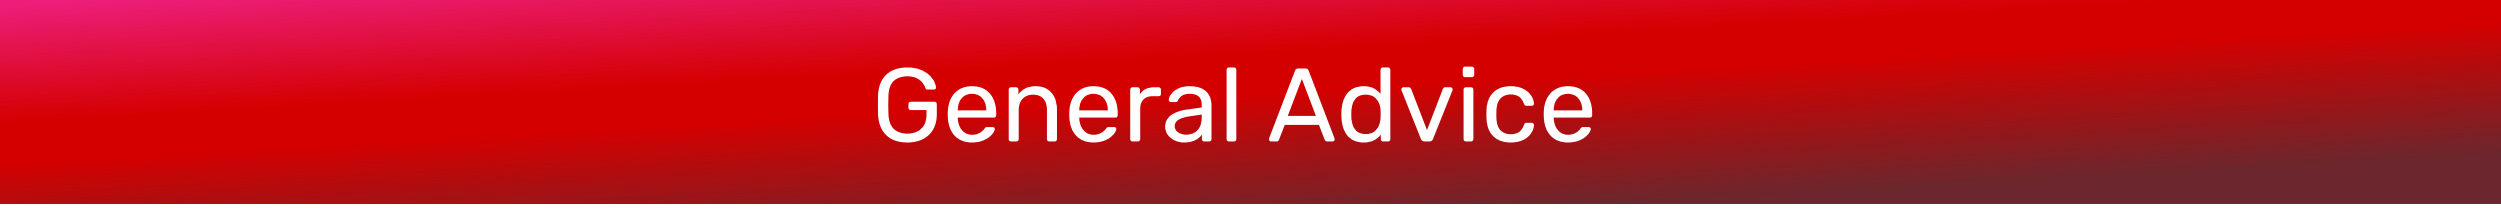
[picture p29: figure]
General Advice

❖ Wait a minute or two after starting the PSLab sensor box ❖ Ensure an active Wi-Fi connection
❖ Access the file server “anonymously”
❖ Choose unique connection names

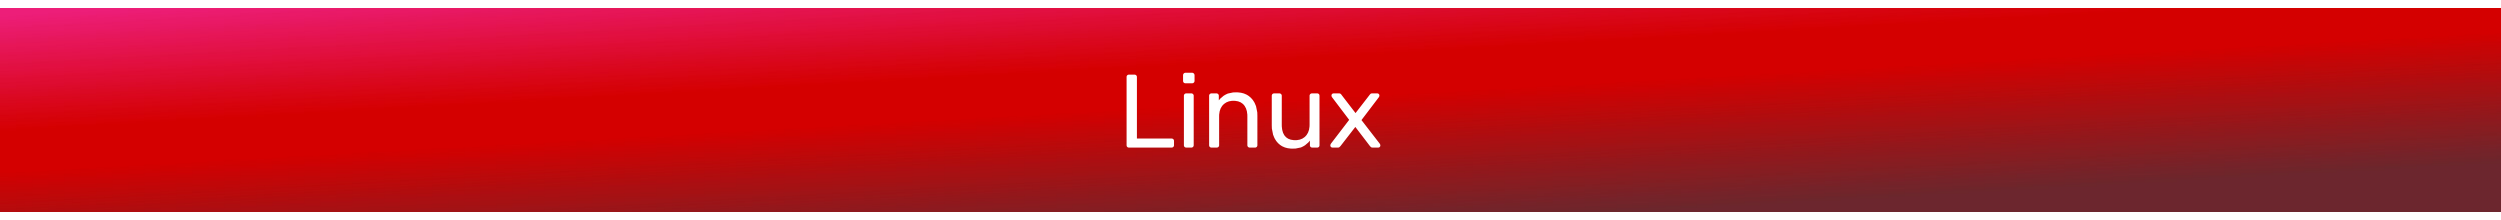
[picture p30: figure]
Linux

❖ Open the file explorer
❖ The new device “PSLab” should automatically appear in the network section (else, refresh the page)
❖ Connect to this device

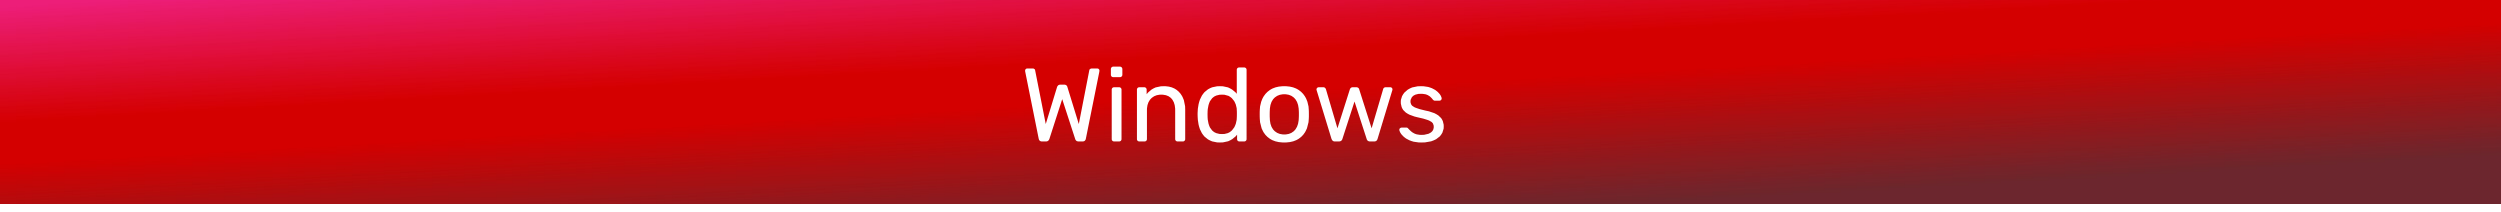
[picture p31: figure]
Windows

❖ Open the file explorer
❖ Right click on "This PC" and select "Add Network Address" ❖ Choose to add a user defined network address and enter "\\...\data" as this address
❖ Assign a name to this new connection

Mac

❖ Hit Command+K and look for "Connect to Server"
❖ Enter "smb://.../data" as the server address and click "Connect"
❖ Confirm the action be entering your login details

iPhone

❖ Open the "Files" app
❖ Select "Browse" > "Connect to Server"
❖ Enter "smb://.../data" as the network address and click "Connect"

Android

❖ Network device support depends on the specific phone type
❖ In case they are not supported, there are several external applications for this use case available in the Play Store or on F-Droid

## Accessing the Data


## Up Next: Advanced Projects for Students

❖ Accessing the Raspberry Pi operating system ❖ Manually running the sensor scripts
❖ Adjusting the measurement interval
❖ Adjusting the flushing interval
❖ Accessing the continuous measurement data stream via an API
❖ Fetching Software Updates from GIT
❖ Changing the sensor type
❖ … and many more


## Experimenting with Python


# Thank you!


https://github.com/fossasia/pslab-scripts Twitter, Github, FB, Linkedin: @pslabio @opntec

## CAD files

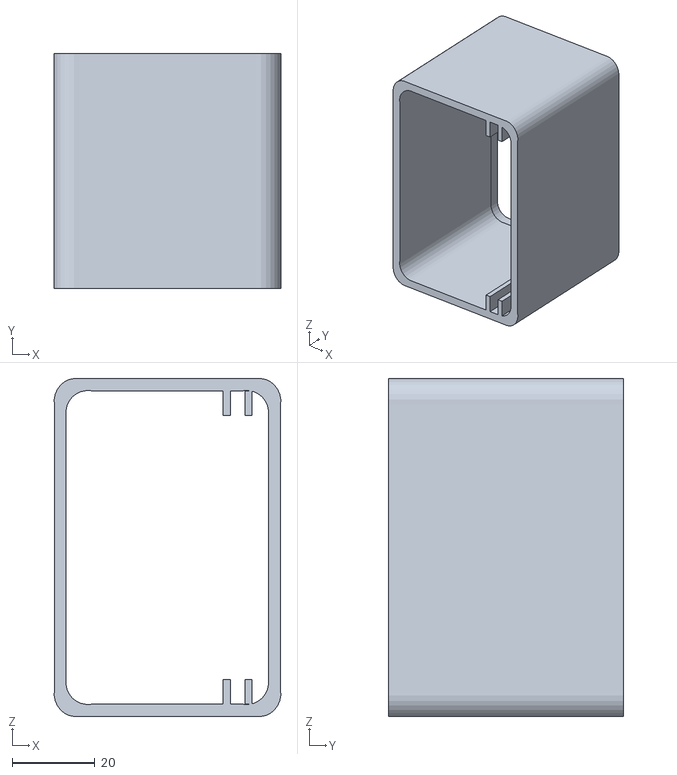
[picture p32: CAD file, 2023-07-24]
docs/casing/box_rail_3.5mm/top.stl
54.9 x 57.0 x 81.9

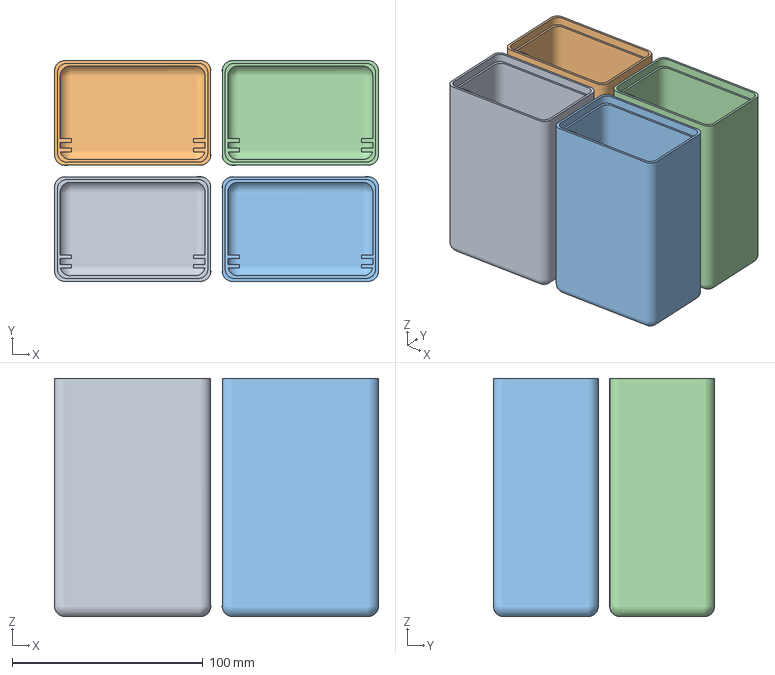
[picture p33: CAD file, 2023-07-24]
docs/casing/box_rail_3mm/prusa_project_file.3mf
170.0 x 116.0 x 125.0 mm
difference_3.stl x 4

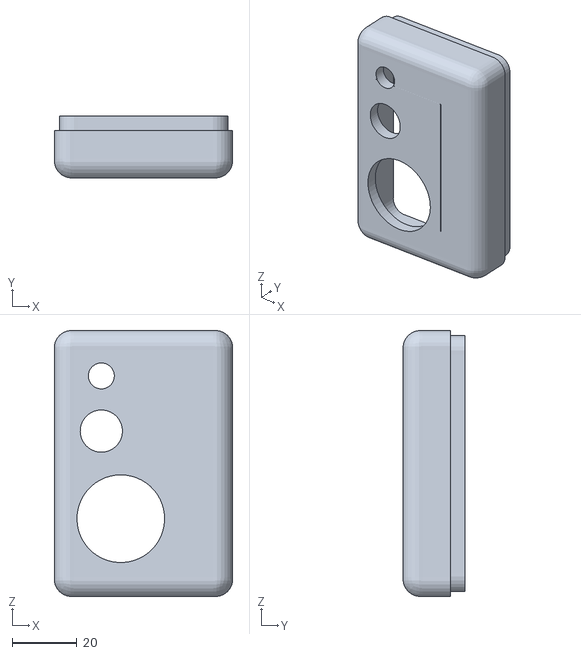
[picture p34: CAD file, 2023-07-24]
docs/casing/lid/lid.stl
55.0 x 19.1 x 82.0

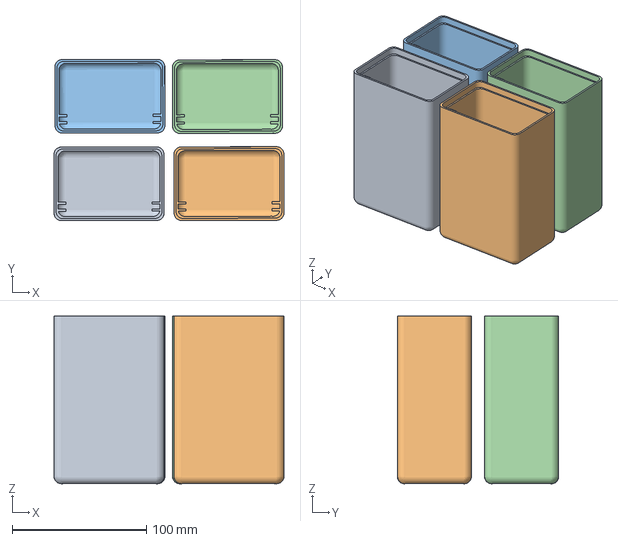
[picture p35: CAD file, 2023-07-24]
docs/casing/box_rail_3.5mm/prusa_project_file.3mf
171.6 x 120.5 x 125.0 mm
difference_2.stl x 4

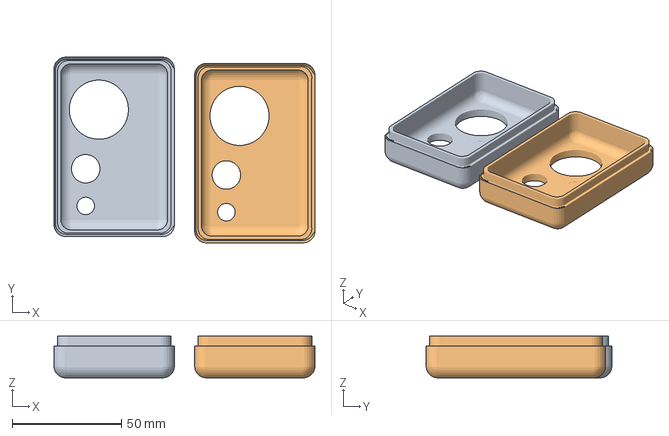
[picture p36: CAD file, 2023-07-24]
docs/casing/lid/prusa_project_file.3mf
119.3 x 84.8 x 19.1 mm
lid.stl x 2

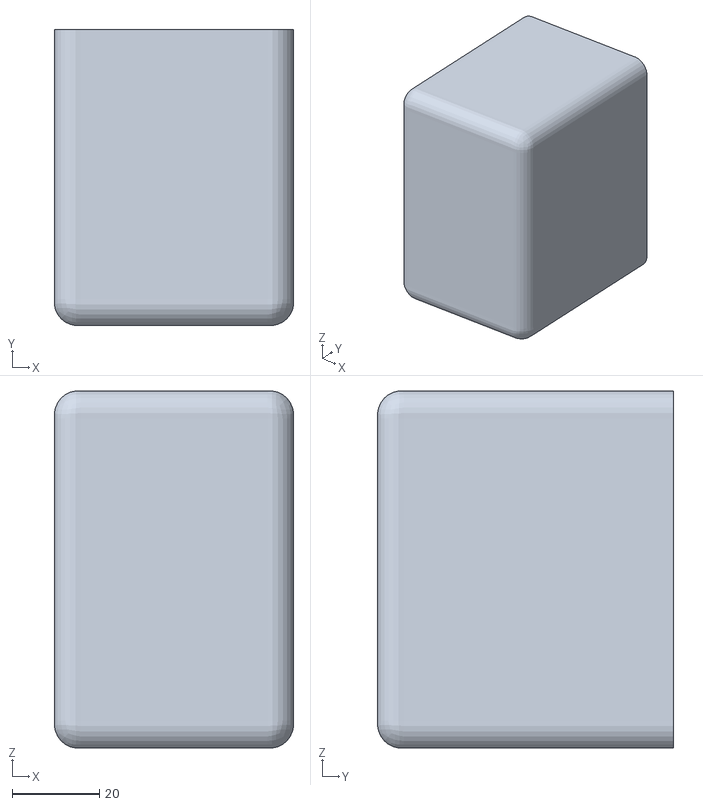
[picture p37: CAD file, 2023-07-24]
docs/casing/box_rail_3.5mm/bottom.stl
55.0 x 68.0 x 82.0

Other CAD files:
docs/casing/box_rail_3mm/top.stl
docs/casing/box_rail_3mm/bottom.stl

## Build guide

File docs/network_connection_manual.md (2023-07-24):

# Connecting a User Device (PC or Phone) to the File Server

Once the PSLab sensor box is connected to a known WiFi Hotspot nearby, its file server is shared over this network and
can be accessed as follows.

## General Disclaimers

1. You probably need to wait a minute or two after starting the PSLab sensor box, until the WiFi connection is successfully initialized.
2. The file server is supposed to be accessed **anonymously**, as a **"guest user"**, without username or password.
3. The connection name can be chosen arbitrarily. Just make sure, that different names are assigned to the different PSLabs, in order for them not to be mixed up.
4. The Raspberry Pi's IP address can be obtained by following the tutorial in the README section about [accessing the Raspberry Pi](/README.md#accessing-the-raspberry-pi).

## On Windows

1. Open the file explorer.
2. Right click on `This PC` and select `Add Network Address`.
3. Choose to add a user defined network address and enter `\\<ip_raspi>\data` as this address.
4. Assign a name to this new connection.
5. Finish the wizard. The PSLab is now available as a network device under `This PC > Network Addresses`.

## On Mac

1. Hit Command+K and look for `Connect to Server`.
2. Enter `smb://<ip_raspi>/data` as the server address and click `Connect`.
3. Confirm the action be entering your login details.

## On Linux

1. Open a terminal.
2. Execute `pip3 install samba`.
3. Open the file explorer.
4. The new device `PSLab` should automatically appear in the `network` section (else: refresh the page via `View > Refresh`). Connect to this device.

## On iPhone

1. Open the `Files` app.
2. Select `Browse` > `Connect to Server`.
3. Enter `smb://<ip_raspi>/data` as the network address and click `Connect`.

## On Android Phone

Depending on the type of phone, the device's preinstalled file explorer may or may not support connections to network devices. In case they are not supported, there are several external applications available in the Play Store, that support this feature. One of them is for example ["EX File Manager"](https://play.google.com/store/apps/details?id=com.ace.ex.file.manager). Here, the shared data of the PSLab Sensor Box can be accessed by entering the app, opening the menu in the top left corner,
selecting `Network > LAN` and clicking on `+ > Scan`.

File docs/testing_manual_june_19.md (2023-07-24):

# Manual for Testing the PSLab Sensor Box Prototypes

The received parcels contain different cardboard boxes with each one device. There are:

- PSLab Sensor Box to [measure Oxygen](./sensors.md#oxygen-sensor-ao-03)
- PSLab Sensor Box to [measure CO2](./sensors.md#co2e-sensor-ccs811)
- PSLab Sensor Box to [measure the temperature](./sensors.md#temperature-sensor-lm35)
- PSLab Sensor Box to [measure light intensity in Lux](./sensors.md#light-intensity-sensor-gl5528)

For each of them the following steps can be executed to test their functionality:

## Opening the Boxes

After opening the paper box, the plastic boxes need to be opened, in order to access the
USB charging connector, the sensor and the power off button. In the final version, those
three items will be exposed outside the box, however right now they are still hidden inside. Opening the plastic box can seem a bit tricky at first, but by angling out the lid from the lower edge (see the description in [advanced usage](../README.md#advanced-usage)) it becomes fairly easy.

<p align="center">
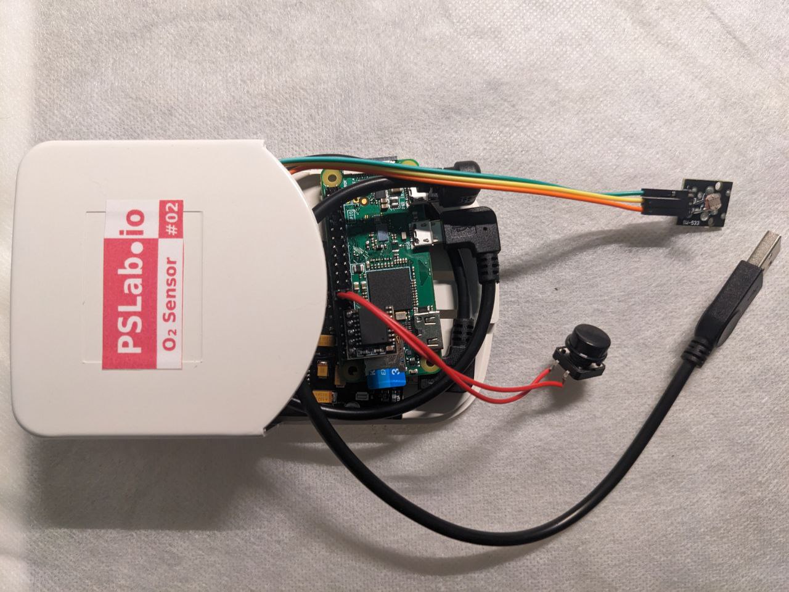
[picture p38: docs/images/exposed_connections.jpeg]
Exposed Connections
    
</p>

## Measuring and Evaluating the Data

Once the box is open and the important parts are exposed, an electricity supply can
be connected to the USB plug. This can for example be a power bank or a laptop. The Raspberry Pi now boots. Please wait a minute for this process to finish.

While the first four devices still use the mechanism to store the measurement data in a CSV
file, those newer devices directly send the data over to a receiver device via the OSC protocol. Therefore the two charges of devices have to be handled differently:

### Older Devices from June 12

- The successfully finished booting process is indicated by a WiFi Hotspot opening up: Please check
on your phone or PC for a new WiFi access point named "PSLab<...>".
- If there is no such WiFi Hotspot visible: Try using another power source for the
PSLab Sensor Box and maybe even another USB charging cable. Please note, that the
glowing lights on the PSLab/ Raspberry Pi do not guarantee a sufficient electricity
supply for all of the device's functionalities.
- Once this WiFi Hotspot can be detected, a connection needs to be established by following the
[connection guide](./network_connection_manual.md). Please make sure to read the
[general disclaimers](./network_connection_manual.md#general-disclaimers) thoroughly,
as those tips can prevent most common issues.

- When booting, the Raspberry Pi created a new measurement file for this session
and directly began to add a new measurement value every second. This file can be found
when accessing the "data" folder within the shared directory of the PSLab sensor box.
More information on this can be found [here](../README.md#basic-usage).
- Now identify the most recent measurement by looking for the file name with the
highest number.
- Test the continuous data serving functionality by opening thus current measurement
file, scrolling down to check the last time stamp, closing the file and opening it again
after a few seconds to check & compare the last time stamp.

### Newer Devices from June 19

- In this version, the device does not open an own WiFi Hotspot, but instead connects to a public
WiFi, in order to make multiple devices accessible at once within one network. Therefore, the devices first need to be connected to a common WiFi access point. This connection is automatically done, once the Raspberry Pi remembers the WiFi, however the first setup needs to be executed manually by connecting the Raspberry Pi to a monitor (as explained [here](../README.md#using-the-raspberry-pi-as-an-independent-computer)) and adding the new network.
- Alternatively, a dummy connection with the credentials "myHotspot" as the SSID and "password123" as the password is already set up. Therefore the device can be tested by just opening a Hotspot from your phone/PC with those credentials. The PSLab Sensor Box will then automatically connect with this network, no monitor connection needed. In case of connection errors, try restarting the Raspberry Pi.
- The PSLab Sensor Box now sends OSC data within this WiFi network. Currently, the receiver of this OSC data is at IP address 192.168.173.152, however this can be edited in the osc_sharing.py file (by connecting the PSLab Sensor Box to a monitor or accessing it via SSH, as described [here](../README.md#accessing-the-raspberry-pi)). A simple server to receive the OSC messages on a PC using python is explained [here](../README.md#receiving-the-osc-messages).

## Up Next

- Detailed information on accessing/ modifying the code and debugging can be found [here](../README.md#advanced-usage).
- Please report all detected bugs and problems to our team.
- We are eager to come over to Weimar to resolve any
remaining issues and give a workshop on how to use the device's full potential.

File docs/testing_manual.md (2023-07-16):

# Manual for Testing the PSLab Sensor Box Prototypes

The received parcels contain different cardboard boxes with each one device. There are:

- PSLab Sensor Box to [measure Oxygen](./sensors.md#oxygen-sensor-ao-03)
- PSLab Sensor Box to [measure CO2](./sensors.md#co2e-sensor-ccs811)
- PSLab Sensor Box to [measure the temperature](./sensors.md#temperature-sensor-lm35)
- PSLab Sensor Box to [measure light intensity in Lux](./sensors.md#light-intensity-sensor-gl5528)

For each of them the following steps can be executed to test their functionality:

## Opening the Boxes

After opening the paper box, the plastic boxes need to be opened, in order to access the
USB charging connector, the sensor and the power off button. In the final version, those
three items will be exposed outside the box, however right now they are still hidden inside. Opening the plastic box can seem a bit tricky at first, but by angling out the lid from the lower edge (see the description [here](../README.md#advanced-usage)) it becomes fairly easy.

<p align="center">
    Exposed Connections
</p>

## Measuring and Evaluating the Data

Once the box is open and the important parts are exposed, an electricity supply can
be connected to the USB plug. This can for example be a power bank or a laptop. The Raspberry Pi now boots. Please wait a minute for this process to finish.

While the first four devices still use the mechanism to store the measurement data in a CSV
file, those newer devices directly send the data over to a receiver device via the OSC protocol. Therefore the two charges of devices have to be handled differently:

### Older Devices from June 12

- The successfully finished booting process is indicated by a WiFi Hotspot opening up: Please check
on your phone or PC for a new WiFi access point named "PSLab<...>".
- If there is no such WiFi Hotspot visible: Try using another power source for the
PSLab Sensor Box and maybe even another USB charging cable. Please note, that the
glowing lights on the PSLab/ Raspberry Pi do not guarantee a sufficient electricity
supply for all of the device's functionalities.
- Once this WiFi Hotspot can be detected, a connection needs to be established by following the
[connection guide](./network_connection_manual.md). Please make sure to read the
[general disclaimers](./network_connection_manual.md#general-disclaimers) thoroughly,
as those tips can prevent most common issues.

- When booting, the Raspberry Pi created a new measurement file for this session
and directly began to add a new measurement value every second. This file can be found
when accessing the "data" folder within the shared directory of the PSLab sensor box.
More information on this can be found [here](../README.md#basic-usage).
- Now identify the most recent measurement by looking for the file name with the
highest number.
- Test the continuous data serving functionality by opening thus current measurement
file, scrolling down to check the last time stamp, closing the file and opening it again
after a few seconds to check & compare the last time stamp.

### Newer Devices from June 19

- In this version, the device does not open an own WiFi Hotspot, but instead connects to a public
WiFi, in order to make multiple devices accessible at once within one network. Therefore, the devices first need to be connected to a common WiFi access point. This connection is automatically done, once the Raspberry Pi remembers the WiFi, however the first setup needs to be executed manually by connecting the Raspberry Pi to a monitor (as explained [here](../README.md#using-the-raspberry-pi-as-an-independent-computer)) and adding the new network.
- Alternatively, a dummy connection with the credentials "myHotspot" as the SSID and "password123" as the password is already set up. Therefore the device can be tested by just opening a Hotspot from your phone/PC with those credentials. The PSLab Sensor Box will then automatically connect with this network, no monitor connection needed. In case of connection errors, try restarting the Raspberry Pi.
- The PSLab Sensor Box now sends OSC data within this WiFi network. Currently, the receiver of this OSC data is at IP address 192.168.173.152, however this can be edited in the osc_sharing.py file (by connecting the PSLab Sensor Box to a monitor or accessing it via SSH, as described [here](../README.md#accessing-the-data-on-the-raspberry-pi)). A simple server to receive the OSC messages on a PC using python is explained [here](../README.md#receiving-the-osc-messages).

## Ending the Measurement

To finish the measurement session, the device needs to be shut down. This can
simply be done by just unplugging the power source, however in the long term,
this technique can be harmful for the Raspberry Pi's file system. We therefore decided to
attach a button to the PSLab Sensor Box. Please press this button for one to two seconds
to trigger the shutdown process of the Raspberry Pi. As that process needs 20-30 seconds,
it is important to wait a bit (until the Raspi's lights went off)
before finally unplugging the electricity source.

## Up Next

- Detailed information on accessing/ modifying the code and debugging can be found [here](../README.md#advanced-usage).
- Please report all detected bugs and problems to our team.
- We are eager to come over to Weimar to resolve any
remaining issues and give a workshop on how to use the device's full potential.

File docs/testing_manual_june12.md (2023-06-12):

# Manual for Testing the PSLab Sensor Box Prototypes

The received parcel contains four different cardboard boxes with each one device:

- one PSLab Sensor Box to [measure Oxygen](./sensors.md#oxygen-sensor-ao-03)
- one PSLab Sensor Box to [measure CO2](./sensors.md#co2e-sensor-ccs811)
- one PSLab Sensor Box to [measure the temperature](./sensors.md#temperature-sensor-lm35)
- one PSLab Sensor Box to [measure light intensity in Lux](./sensors.md#light-intensity-sensor-gl5528)

For each of them the following steps can be executed to test their functionality:

## Opening the Boxes

After opening the paper box, the plastic boxes need to be opened, in order to access the
USB charging connector, the sensor and the power off button. In the final version, those
three items will be exposed outside the box, however right now they are still hidden inside. Opening the plastic box can seem a bit tricky at first, but by angling out the lid from the lower edge (see the description [here](../README.md#advanced-usage)) it becomes fairly easy.

<p align="center">
    Exposed Connections
</p>

## Startup and Establishing a Connection

- Once the box is open and the important parts are exposed, an electricity supply can
be connected to the USB plug. This can for example be a power bank or a laptop.
- The Raspberry Pi now boots. Please wait a minute for this process to finish.
- The successfully finished booting process is indicated by a WiFi Hotspot opening up: Please check
on your phone or PC for a new WiFi access point named "PSLab<...>".
- If there is no such WiFi Hotspot visible: Try using another power source for the
PSLab Sensor Box and maybe even another USB charging cable. Please note, that the
glowing lights on the PSLab/ Raspberry Pi do not guarantee a sufficient electricity
supply for all of the device's functionalities.
- Once this WiFi Hotspot can be detected, a connection needs to be established by following the
[connection guide](./network_connection_manual.md). Please make sure to read the
[general disclaimers](./network_connection_manual.md#general-disclaimers) thoroughly,
as those tips can prevent most common issues.

## Collecting Measurement Data

- When booting, the Raspberry Pi created a new measurement file for this session
and directly began to add a new measurement value every second. This file can be found
when accessing the "data" folder within the shared directory of the PSLab sensor box.
More information on this can be found [here](../README.md#basic-usage).
- Now identify the most recent measurement by looking for the file name with the
highest number.
- Test the continuous data serving functionality by opening thus current measurement
file, scrolling down to check the last time stamp, closing the file and opening it again
after a few seconds to check & compare the last time stamp.

## Ending the Measurement

To finish the measurement session, the device needs to be shut down. This can
simply be done by just unplugging the power source, however in the long term,
this technique can be harmful for the Raspberry Pi's file system. We therefore decided to
attach a button to the PSLab Sensor Box. Please press this button for one to two seconds
to trigger the shutdown process of the Raspberry Pi. As that process needs 20-30 seconds,
it is important to wait a bit (until the Raspi's lights went off)
before finally unplugging the electricity source.

## Up Next

- Detailed information on accessing/ modifying the code and debugging can be found [here](../README.md#advanced-usage).
- Please report all detected bugs and problems to our team.
- We are currently working on the next version of the PSLab Sensor Boxes that will support the OSC protocol, as
well as the functionality to connect multiple devices at once to a (public)
WiFi network. This new version will arrive in Weimar until June 17.
- Once this OSC version is ready, we are eager to come over to Weimar to resolve any
remaining issues and give a workshop on how to use the device's full potential.

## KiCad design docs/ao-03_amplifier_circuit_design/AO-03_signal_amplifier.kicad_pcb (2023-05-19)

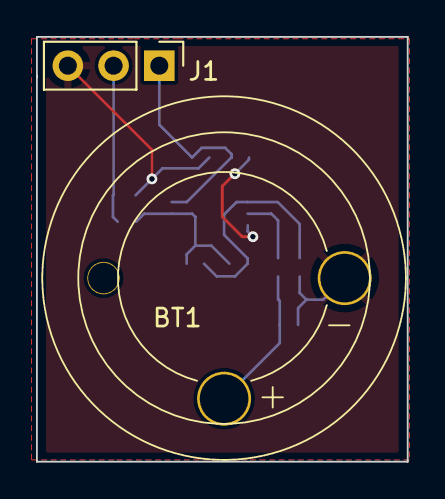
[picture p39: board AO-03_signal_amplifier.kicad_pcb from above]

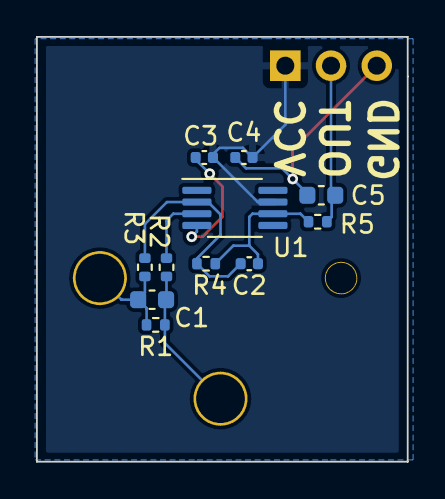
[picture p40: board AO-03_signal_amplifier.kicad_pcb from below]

Board: 2 copper layers, 20.6 x 23.6 mm, 13 parts (11 on the bottom side), 7 nets.

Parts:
BT1: AO3(Oxygen sensor); AO-03
C1: 4.7u; C_0603_1608Metric
C2, C3: 10n; C_0402_1005Metric
C4: 100n; C_0402_1005Metric
C5: 10u; C_0603_1608Metric
J1: Conn_01x03; PinHeader_1x03_P2.54mm_Vertical
R1, R5: 100; R_0402_1005Metric
R2, R3: 10k; R_0402_1005Metric
R4: 400k; R_0402_1005Metric
U1: AD8551ARM; MSOP-8_3x3mm_P0.65mm

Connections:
/OUT: C5.1, J1.2, R5.2
GND: BT1.2 (-), C1.2, C3.2, C4.2, C5.2, J1.3, R1.1, R3.1, U1.4 (V-)
unnamed: BT1.1 (+), C1.1, R1.2, R2.1
unnamed: C2.1, R3.2, R4.1, U1.2 (-)
unnamed: C2.2, R4.2, R5.1, U1.6
unnamed: R2.2, U1.3 (+)
VCC: C3.1, C4.1, J1.1, U1.7 (V+)

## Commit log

2018-10-08 fixes #115 and also de-indented the code by 2 spaces
2018-10-10 Inserted new lines and fixes #115
2023-05-18 add device logos
2023-05-19 fix: renaming the sensor files to lower case
2023-05-19 add support for L35 temperature sensor
2023-05-19 Add script for CCS811 eCO2 and eTVOC sensor
2023-05-19 Add project document for AO-03 oxygen sensor
    [AO-03_signal_amplifier.kicad_pcb, AO-03_signal_amplifier.kicad_sch]
2023-05-19 embedding the CO2 sensor into the routine
2023-05-19 fix: allowing CO2 sensor to fail once
2023-05-21 update documentation images
    [AO-03_signal_amplifier.kicad_pcb, AO-03_signal_amplifier.kicad_sch]
2023-05-26 add images for sensor connections
2023-06-12 add testing manual for prototype version
2023-06-16 re-calibrating the light sensor
2023-07-19 updating docs
    [body.stl, lid.stl]
2023-07-19 recalibrating new oxygen sensors
2023-07-20 add sensor color codes
2023-07-21 recalibrating oxygen sensor
2023-07-24 add casing files
    [bottom.stl, lid.stl, prusa_project_file.3mf, top.stl]
2023-07-24 update images
    [body.stl, lid.stl]
2023-07-24 updating sensor connection documentation
